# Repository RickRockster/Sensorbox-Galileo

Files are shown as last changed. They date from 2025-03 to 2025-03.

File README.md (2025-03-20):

# Sensorbox-Galileo
Nach dem erreichen vom 2. Platz bei Jugend-forscht nun der Code, die 3mf. Dateien und eine Anleitung (folgt noch!).

# Was ist die Sensorbox?
Im Physikunterricht ist Teil des Lehrplans die digitale Messwerterfassung. Die vorhanden Sensoren sind allerdings sehr teuer. Der Galileo ersetzt diese Lösungen für 45€. beigefügt ist eine Liste aller benötigten Sensoren. 

# Materialliste
| Komponent | Funktion/Beschreibung |
| ------------- | ------------- |
| Arduino Nano ESP32 | Mikrocontroller |
| Steckbrett | Zum befestigen der Sensoren *  |
| VL53LXX-V2  | Abstandssensor  |
| PDV-P8104  | Fotowiderstand  |
| KY-035  | Mangetfeldsensor  |
| MAX6675   | Temperatursensor  |
| Jumper-Wires  | Kabel  |
| Filament (PLA)  |  für 3D-Druck   |
| Knopf/Schalter  |  für den Sensorwechsel   |

*Steckbrett ist ggf. austauschbar, falls man es auf einem PCB oder ähnlichem Bauen möchte

# Pinbelegung

| MAX6675-Pin | Arduino Nano-Pin |
|     :---:      |     :---:      |
| SO  | D7  |
| CS  | D9  |
| SCK  | D8  |
| VCC  | 3.3V  |
| GND  | GND  |

<br /> 
<br /> 

| KY-035-Pin  | Arduino Nano-Pin |
|     :---:      |     :---:      |
| GND  | GND  |
| VIN  | 3.3V  |
| S  | A0  |

<br /> 
<br /> 

| Fotowiderstand-Pin  | Arduino Nano-Pin |
|     :---:      |     :---:      |
| PIN 1  | 3.3V |
| PIN 2  | A3  |

zwischen den zweiten Pin des Fotowiderstandes noch einen 1KOhm-Widerstand in GND des Arduinos

Bei dem Fotowiderstand sind beide Pins identisch. Welcher für was verwendet wird ist irrelevant. 

<br /> 
<br /> 

| VL53LXX-V2-Pin  | Arduino Nano-Pin |
|     :---:      |     :---:      |
| VIN  | 3.3V  |
| GND  | GND  |
| SCL  | A5  |
| SDA  | A4  |

<br /> 
<br /> 

| Knopf/Schalter  | Arduino Nano-Pin |
|     :---:      |     :---:      |
| PIN 1 (meist rot)  | 3.3V  |
| PIN 2 (meist schwarz)  | A7  |

Knopf kann nach belieben ausgewählt werden. Bei meinem Gehäuse habe ich folgenden Knopf verwendet:
https://www.amazon.de/dp/B08L49F7DV?th=1

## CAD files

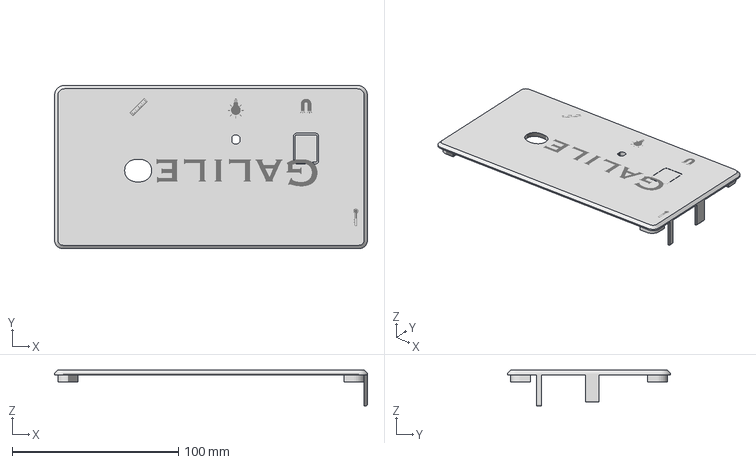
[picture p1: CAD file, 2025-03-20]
Deckel.3mf
188.0 x 98.0 x 21.4 mm

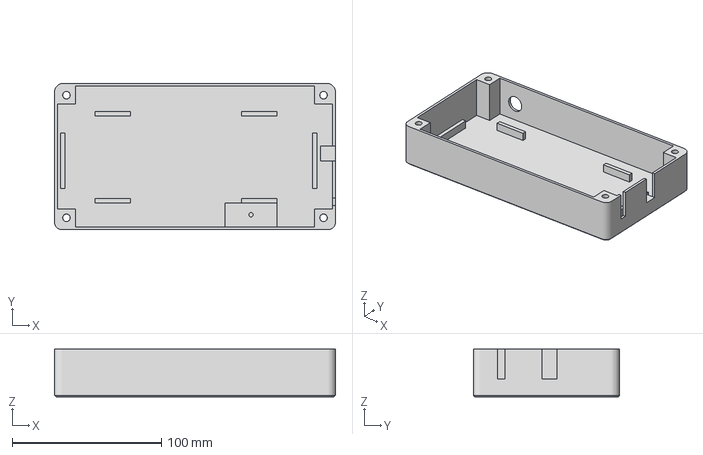
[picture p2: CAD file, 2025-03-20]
Unter-Teil.3mf
188.0 x 98.0 x 32.0 mm

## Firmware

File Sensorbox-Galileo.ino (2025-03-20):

#include "Adafruit_VL53L0X.h"
#include <phyphoxBle.h>
#include "max6675.h"

//Pins von: CLK, CS, SO
MAX6675 ktc(8, 9, 7);

Adafruit_VL53L0X lox = Adafruit_VL53L0X();

//Um die Debug Ausgaben zu aktivieren
//muss dieser Wert auf "true" gesetzt werden.
#define debugSensor false

//button
  const int buttonPin = A7;
  int menuState = 1;
  float menuVal;
  bool buttonPressed = false;
  const int debounceTime = 200; 
  unsigned long lastPressTime = 0;

//laser
  //Es werden 10 Messungen durchgeführt.
  const int MAX_DATA = 10;
  //der Index der aktuellen Messung
  int readDataIndex = -1;
  //das Array für die Daten
  int data[MAX_DATA] = {};
  float averagelaser;

  //zählen der fehlerhaften Messungen
  int failureMeasures = 0;
  bool sensorstate = true;
  const int red = 6;
  const int green = 3;
  const int button = 2;
  int buttonread;
  int lastButtonState = false;

//Magnetsensor
  const int magnetpin = A0;
  int state = 0;
  float newstate = 0;
//Photoresistor

  float photostate = 0;
  const int photoresistorPin = A3;

//Temperatursensor

  float temperature;
void setup() {
  //begin der seriellen Kommunikation mit 115200 baud
  Serial.begin(115200);
  Serial.println("TEST");
  pinMode(magnetpin, INPUT);
  pinMode(buttonPin, INPUT);

  Phyphox();
  //Warten auf den Seriellen Port


  //Wenn der Serielle Port bereit ist dann eine Ausgabe auf diesen tätigen
  //und prüfen ob der Sensor korrekt angeschlossen ist (ob dieser Ansprechbar ist)
  Serial.println("GY-VL53L0X test");
  if (!lox.begin()) {
    Serial.println("Fehler beim lesen des Sensors!");
    while (1)
      ;  //eine Endlos Schleife
  }
}

void loop() {

  SensorstateSwitch();

  PhyphoxBLE::write(averagelaser, newstate, photostate, temperature, menuVal);
}

void laser() {
  VL53L0X_RangingMeasurementData_t measure;
  lox.rangingTest(&measure, debugSensor);

  //lesen des Sensor Status
  //der Sensor kann verschiedene Status annehmen,
  //jedoch interessiert für uns nur der Wert "4"
  int sensorStatus = measure.RangeStatus;
  
  //Wenn Daten empfangen wurden dann...
  if (sensorStatus != VL53L0X_DEVICEERROR_MSRCNOTARGET) {
    //den Zähler für das Array um eins erhöhen
    readDataIndex++;
    //zuweisen des Wertes in das Array
    data[readDataIndex] = measure.RangeMilliMeter;

    //Wenn das Array "fertig" befüllt ist, dann...
    if (readDataIndex == MAX_DATA) {
      //eine Variable für die Berechnung des Durchschnittswertes
      float averageData = 0;
      //über das Array itereieren und die Daten zusammenzählen
      for (int i = 0; i < MAX_DATA; i++) {
        averageData = averageData + data[i];
      }
      //um den Durchschnittswert zu erhalten muss man die Zahl
      //durch die Anzahl der Werte teilen
      averageData = averageData / MAX_DATA;
      //Ausgeben des berechnenen Durchschnitts für die Distanz

      averagelaser = averageData / 10 - 2,5;

      //Serial.println("cm");
      readDataIndex = -1;
      failureMeasures = 0;
    } else if (debugSensor && readDataIndex % 2 == 0) {
      Serial.print("X");
    }
  } else if (debugSensor && sensorStatus != VL53L0X_DEVICEERROR_NONE) {
    Serial.println(" Signal konnte nicht gelesen / verarbeitet werden! ");
  } else {
    if (debugSensor && ++failureMeasures % 2 == 0) {
      Serial.print("-");
    }
  }

  if (debugSensor && (failureMeasures + readDataIndex) > MAX_DATA) {
    Serial.println("");
  }
}

void Phyphox() {
  PhyphoxBLE::start("Galileo");

  PhyphoxBleExperiment AbstandExp;

  AbstandExp.setTitle("Galileo");
  AbstandExp.setCategory("Arduino Experiments");
  AbstandExp.setDescription("Hier drin sind ein paar Experimente der Galileo-Box!");

  PhyphoxBleExperiment::View firstView;
  firstView.setLabel("Abstand");  //Create a "view"
  PhyphoxBleExperiment::View secondView;
  secondView.setLabel("Magnetfeld");
  PhyphoxBleExperiment::View thirdView;
  thirdView.setLabel("Lichtstärke");
  PhyphoxBleExperiment::View fourthView;
  fourthView.setLabel("Temperatur");

  PhyphoxBleExperiment::Graph firstGraph;
  firstGraph.setMinY(0, LAYOUT_FIXED);
  firstGraph.setMaxY(120, LAYOUT_FIXED);
  firstGraph.setLabel("Abstand");
  firstGraph.setUnitX("s");
  firstGraph.setUnitY("cm");
  firstGraph.setLabelX("Zeit");
  firstGraph.setLabelY("Abstand");
  firstGraph.setXPrecision(1);
  firstGraph.setYPrecision(1);

  firstGraph.setChannel(0, 1);

  PhyphoxBleExperiment::Separator LaserSeparator;  //Creates a line to separate elements.
  LaserSeparator.setHeight(2);                     //Sets height of the separator.
  LaserSeparator.setColor("404040");

  PhyphoxBleExperiment::Separator MagnetSeparator;  //Creates a line to separate elements.
  MagnetSeparator.setHeight(2);                     //Sets height of the separator.
  MagnetSeparator.setColor("404040");

  PhyphoxBleExperiment::Separator LichtSeparator;  //Creates a line to separate elements.
  MagnetSeparator.setHeight(2);                    //Sets height of the separator.
  MagnetSeparator.setColor("404040");

  PhyphoxBleExperiment::Separator TempSeparator;
  TempSeparator.setHeight(2);
  TempSeparator.setColor("404040");

  PhyphoxBleExperiment::Separator TextSeparator1;
  TextSeparator1.setHeight(0.5);
  TextSeparator1.setColor("404040");

  PhyphoxBleExperiment::Separator MenuSeparator;
  MenuSeparator.setHeight(2);
  MenuSeparator.setColor("404040");


  PhyphoxBleExperiment::Graph secondGraph;  //Create graph which will plot random numbers over time
  secondGraph.setLabel("Strength");
  secondGraph.setUnitX("s");
  secondGraph.setUnitY("");
  secondGraph.setLabelX("Zeit");
  secondGraph.setLabelY("Stärke");
  secondGraph.setXPrecision(1);  //The amount of digits shown after the decimal point
  secondGraph.setYPrecision(1);

  secondGraph.setChannel(0, 2);

  PhyphoxBleExperiment::Graph thirdGraph;
  thirdGraph.setMinY(0, LAYOUT_FIXED);
  thirdGraph.setLabelX("Zeit");
  thirdGraph.setLabelY("Lichtstärke");
  thirdGraph.setLabel("Lichtstärke");
  thirdGraph.setUnitX("s");
  thirdGraph.setUnitY("");
  thirdGraph.setXPrecision(1);
  thirdGraph.setYPrecision(1);

  thirdGraph.setChannel(0, 3);

  PhyphoxBleExperiment::Graph fourthGraph;
  fourthGraph.setLabelX("Zeit");
  fourthGraph.setLabelY("Temperatur");
  fourthGraph.setLabel("Temperatur");
  fourthGraph.setUnitX("s");
  fourthGraph.setUnitY("°C");
  fourthGraph.setXPrecision(2);
  fourthGraph.setYPrecision(2);

  fourthGraph.setChannel(0, 4);

  PhyphoxBleExperiment::Value LaserValue;  //Creates a value-box.
  LaserValue.setLabel("Abstand:");         //Sets the label
  LaserValue.setPrecision(1);              //The amount of digits shown after the decimal point.
  LaserValue.setUnit("cm");                //The physical unit associated with the displayed value.
  LaserValue.setColor("FFFFFF");           //Sets font color. Uses a 6 digit hexadecimal value in "quotation marks".
  LaserValue.setChannel(1);
  LaserValue.setXMLAttribute("size=\"2\"");

  PhyphoxBleExperiment::Value MagnetValue;  //Creates a value-box.
  MagnetValue.setLabel("Stärke:");          //Sets the label
  MagnetValue.setPrecision(1);              //The amount of digits shown after the decimal point.
  MagnetValue.setUnit("");                  //The physical unit associated with the displayed value.
  MagnetValue.setColor("FFFFFF");           //Sets font color. Uses a 6 digit hexadecimal value in "quotation marks".
  MagnetValue.setChannel(2);
  MagnetValue.setXMLAttribute("size=\"2\"");

  PhyphoxBleExperiment::Value LichtValue;
  LichtValue.setLabel("Lichtstärke: ");
  LichtValue.setPrecision(1);
  LichtValue.setUnit("");
  LichtValue.setColor("FFFFFF");  //Sets font color. Uses a 6 digit hexadecimal value in "quotation marks".
  LichtValue.setChannel(3);
  LichtValue.setXMLAttribute("size=\"2\"");

  PhyphoxBleExperiment::Value TempValue;
  TempValue.setLabel("Temperatur: ");
  TempValue.setPrecision(2);
  TempValue.setUnit("°C");
  TempValue.setColor("FFFFFF");
  TempValue.setChannel(4);
  TempValue.setXMLAttribute("size=\"2\"");

  PhyphoxBleExperiment::Value MenuValue;
  MenuValue.setLabel("aktueller Sensor: ");
  MenuValue.setPrecision(0);
  MenuValue.setColor("FFFFFF");
  MenuValue.setChannel(5);
  MenuValue.setXMLAttribute("size=\"2\"");

  PhyphoxBleExperiment::InfoField Sensor1;
  Sensor1.setInfo("1: Abstandsmessung");
  Sensor1.setColor("ffffff");
  Sensor1.setXMLAttribute("size=\"1.2\"");

  PhyphoxBleExperiment::InfoField Sensor2;
  Sensor2.setInfo("2: Magnetfeldmessung");
  Sensor2.setColor("ffffff");
  Sensor2.setXMLAttribute("size=\"1.2\"");

  PhyphoxBleExperiment::InfoField Sensor3;
  Sensor3.setInfo("3: Helligkeitsmessung");
  Sensor3.setColor("ffffff");
  Sensor3.setXMLAttribute("size=\"1.2\"");

  PhyphoxBleExperiment::InfoField Sensor4;
  Sensor4.setInfo("4: Temperaturmessung");
  Sensor4.setColor("ffffff");
  Sensor4.setXMLAttribute("size=\"1.2\"");


  PhyphoxBleExperiment::ExportSet mySet;  //Provides exporting the data to excel etc.
  mySet.setLabel("mySet");
  PhyphoxBleExperiment::ExportData myData1;
  myData1.setLabel("myData1");
  myData1.setDatachannel(1);

  firstView.addElement(firstGraph);
  firstView.addElement(LaserSeparator);  //attach graph to view
  firstView.addElement(LaserValue);
  firstView.addElement(MenuSeparator);
  firstView.addElement(MenuValue);
  firstView.addElement(TextSeparator1);
  firstView.addElement(Sensor1);
  firstView.addElement(TextSeparator1);
  firstView.addElement(Sensor2);
  firstView.addElement(TextSeparator1);
  firstView.addElement(Sensor3);
  firstView.addElement(TextSeparator1);
  firstView.addElement(Sensor4);
  secondView.addElement(secondGraph);
  secondView.addElement(MagnetSeparator);
  secondView.addElement(MagnetValue);
  secondView.addElement(MenuSeparator);
  secondView.addElement(MenuValue);
  secondView.addElement(TextSeparator1);
  secondView.addElement(Sensor1);
  secondView.addElement(TextSeparator1);
  secondView.addElement(Sensor2);
  secondView.addElement(TextSeparator1);
  secondView.addElement(Sensor3);
  secondView.addElement(TextSeparator1);
  secondView.addElement(Sensor4);
  thirdView.addElement(thirdGraph);
  thirdView.addElement(LichtSeparator);
  thirdView.addElement(LichtValue);
  thirdView.addElement(MenuSeparator);
  thirdView.addElement(MenuValue);
  thirdView.addElement(TextSeparator1);
  thirdView.addElement(Sensor1);
  thirdView.addElement(TextSeparator1);
  thirdView.addElement(Sensor2);
  thirdView.addElement(TextSeparator1);
  thirdView.addElement(Sensor3);
  thirdView.addElement(TextSeparator1);
  thirdView.addElement(Sensor4);
  fourthView.addElement(fourthGraph);
  fourthView.addElement(TempSeparator);
  fourthView.addElement(TempValue);
  fourthView.addElement(MenuSeparator);
  fourthView.addElement(MenuValue);
  fourthView.addElement(TextSeparator1);
  fourthView.addElement(Sensor1);
  fourthView.addElement(TextSeparator1);
  fourthView.addElement(Sensor2);
  fourthView.addElement(TextSeparator1);
  fourthView.addElement(Sensor3);
  fourthView.addElement(TextSeparator1);
  fourthView.addElement(Sensor4);

  AbstandExp.addView(firstView);
  AbstandExp.addView(secondView);
  AbstandExp.addView(thirdView);  //attach data to exportSet
  AbstandExp.addView(fourthView);
  AbstandExp.addExportSet(mySet);  //attach exportSet to experiment
  PhyphoxBLE::addExperiment(AbstandExp);

  //Channel 0 = Zeit die Daten werden von Phyphox empfagen
  //Channel 1-N Die Daten die mit PhyphoxBLE::write("float") geschrieben werden
}

void Magnet() {
  state = analogRead(magnetpin);

  newstate = (map(state, 0, 4500, -2000, 2000) + 240);//Wert auf Nullbringen


  delay(100);
}

void Photoresistor() {
  photostate = analogRead(photoresistorPin);
}

void Temperatursensor() {
  temperature = ktc.readCelsius();

  delay(250);
}

void SensorstateSwitch() {
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
